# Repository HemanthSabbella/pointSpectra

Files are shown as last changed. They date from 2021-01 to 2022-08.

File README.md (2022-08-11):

# pointSpectra
pointSpectra is a low-cost, open-source alternative for measuring absorbance of the analyte at specific wavelengths of light. This project is initially made to detect various snake species venom in human blood to do a one-to-one mapping of venom and the snake species using Venom Detection Kit. Nevertheless, it  can be used for any analyte.

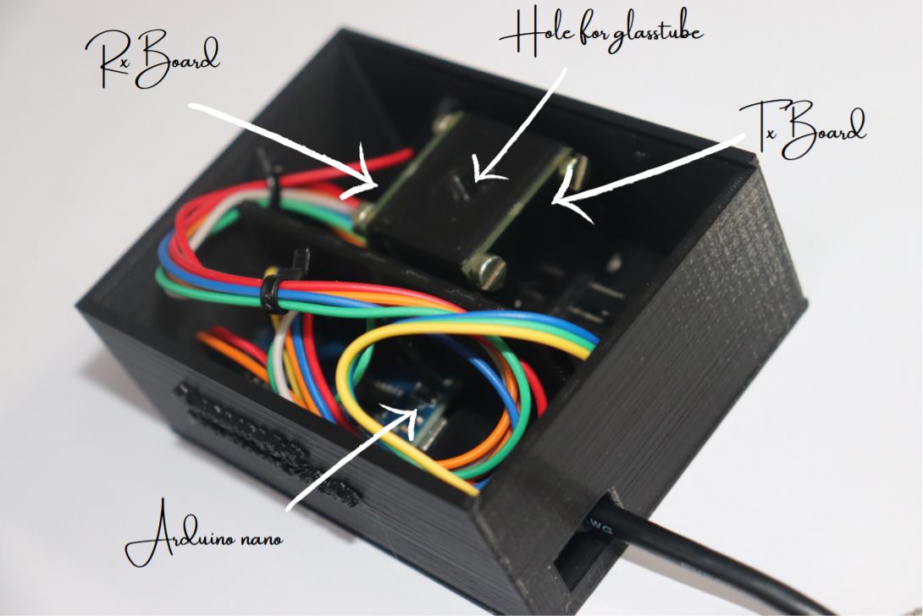
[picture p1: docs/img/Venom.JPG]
> 

**Note:** The whole setup can be built with BOM cost not more than 1000 INR i.e. 15 USD.

# Background

pointSpectra works on the Beer-Lambert law which states that the quantity of light absorbed by a substance dissolved in a fully transmitting solvent is directly proportional to the concentration of the substance and the path length of the light through the solution. The below is the formulation for absorbance of an analyte: 

**Transmittance:**
`T = I / I0`
`% Transmittance: %T = 100 T`

**Absorbance:**
`A = log10 (I0/I)`
`A = log10 (1/T) = -log10 (T)`
`A = log10 (100/%T)`
`A = 2 - log10 (%T)`

# Requirements

**Hardware requirements:**
- [Arduino nano](https://store.arduino.cc/usa/arduino-nano) or [any small form factor arduino](https://store.arduino.cc/usa/arduino/boards-modules)
- [Tx and Rx boards](https://github.com/HemanthSabbella/pointSpectra/tree/main/Tx_Rx_boards%20V1.0)

**Software requirements:**
- [Arduino IDE](https://www.arduino.cc/en/software/)
- [Firmware](https://github.com/HemanthSabbella/pointSpectra/tree/main/firmware)

**Mechanical requirements:**
- [3D-printed case](https://github.com/HemanthSabbella/pointSpectra/tree/main/3D_printed_casing)
- A glass testtube of diameter 5mm.
- Four M3 screws.

# Making 
The setup mainly invoves three boards - Tx Board, Rx Board and Arduino nano. Tx board has wavelength-specific LED emitters that goes through mechanical slits of the 3D printed case in which a glass tube is inserted orthogonally and the unabsorbed light beams coming through the tube, fall on Rx board which has photo diode array that converts the light intensity into proportional frequency. This signal is caputured by the nano-microcontroller, further processing of the data is done and it's followed by plotting the absorbance graph.  

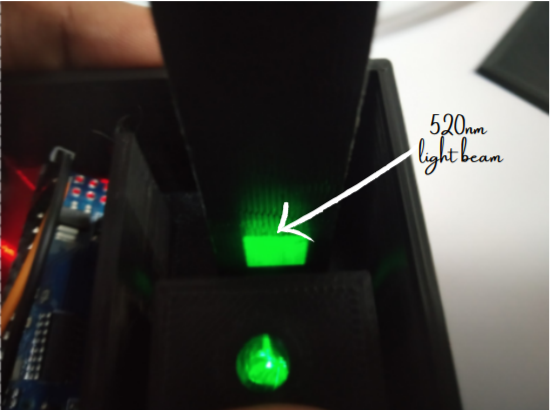
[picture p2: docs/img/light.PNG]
> 
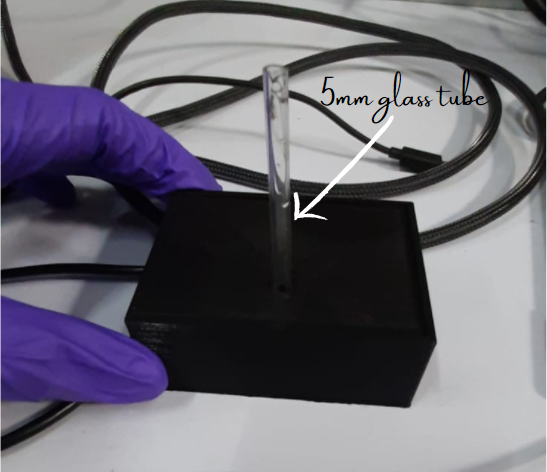
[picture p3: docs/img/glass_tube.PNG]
> 

**Tx Board:** 
- Use narrow-band, dominant wavelength LEDs as light sources for a specific wavelength absorbance. 
- 6-point light sources. 
- Adjust the current limiting resistor properly by using forward voltage and current of LEDs, and the supply voltage. 

Spectral Response of 520nm LED: 

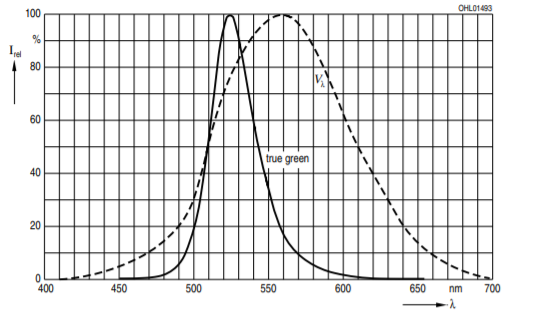
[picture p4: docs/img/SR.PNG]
> 
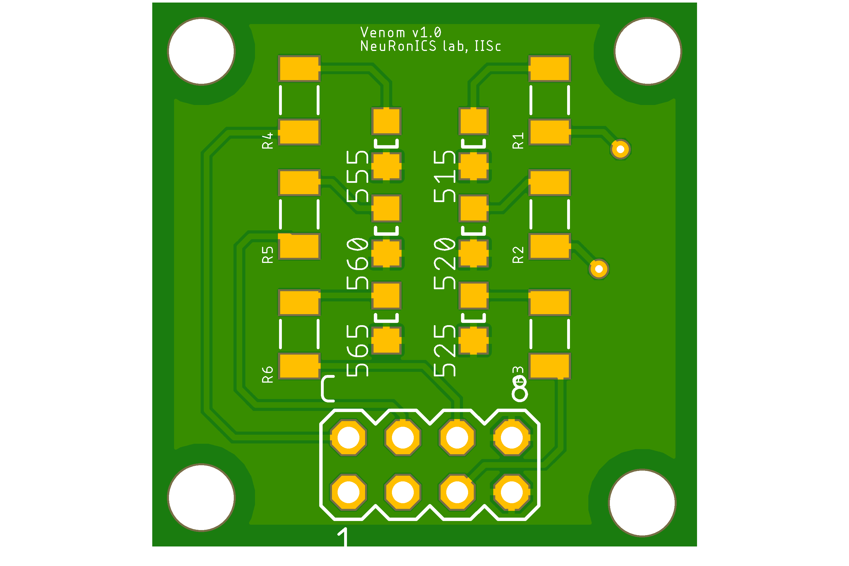
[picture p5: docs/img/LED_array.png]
> 

**Rx Board:**

- TCS3200 - Light (irradiance) to frequency converter. 
- 8 x 8 array of photodiodes. 
- 16 blue filters, 16 green filters, 16 red filters and 16 clear filters. 
- The output is a square wave (50% duty cycle) with frequency directly proportional to luminous intensity (irradiance).

Functional Block Diagram: 

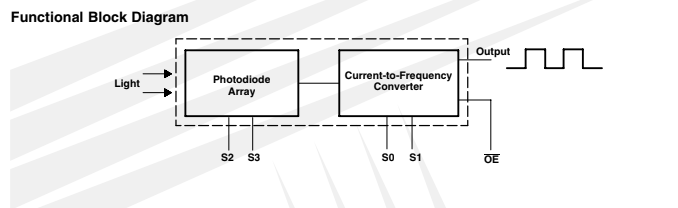
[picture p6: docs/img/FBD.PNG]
> 
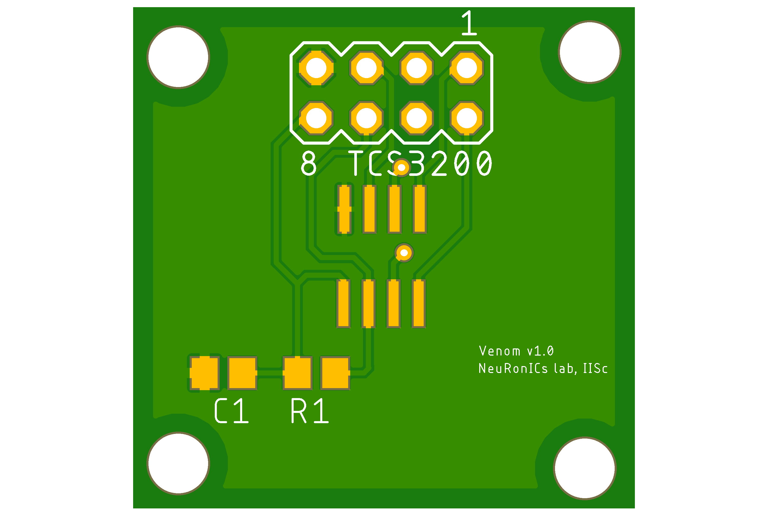
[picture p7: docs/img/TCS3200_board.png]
> 

**3D printed case:**

Use the [cheat sheet](https://github.com/HemanthSabbella/pointSpectra/blob/main/docs/img/3d_print_CS.PNG) of if you are not familiar with 3D printing. We have used fractal works extended printer and print time with infill 50% and layer height 0.2 is 8 hrs. 
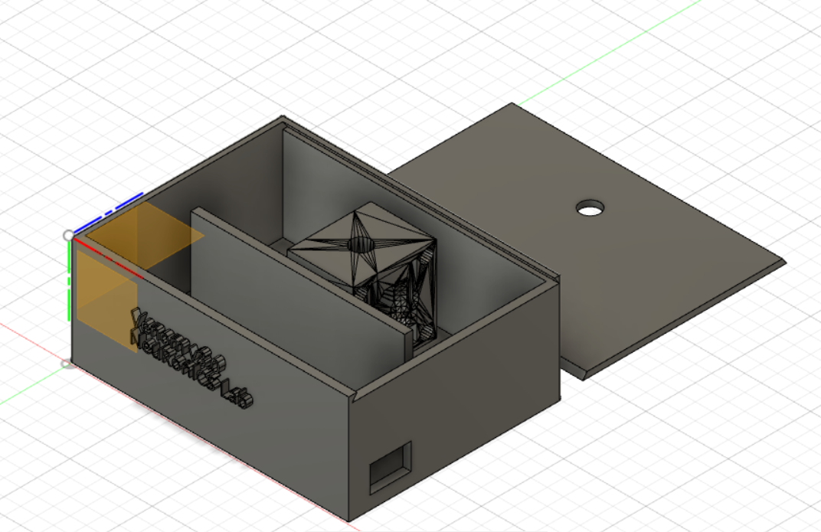
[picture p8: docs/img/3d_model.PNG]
> 

**Pin connections:**

| Tx | Arduino nano|
|------|---------|
| LED_520 | D11 |
| LED_560 | D3 |
| LED_600 | D4 |
| LED_630 | D10 |
| LED_660 | D2 |
| GND | GND |
  
| Rx | Arduino nano|
|--------|---------|
| S0 | D5 |
| S1 | D6 |
| S2 | D7 |
| S3 | D8 |
| sensorOut | D9 |

# Firmware
 The firmware code makes the luminous intensity of LEDs same by adjusting the average current to the LEDs using Pulse Width Modulation (PWM) signals. Standard signal conditioning like moving average on the real-time data is preformed to avoid sharp transition due to external environment. Calibration methods - zero referencing and range mapping are used. It outputs an absorbance graph of an analyte by interpolating the sensor reading of 6 narrow band LED inputs. Flash the [Firmware](https://github.com/HemanthSabbella/pointSpectra/tree/main/firmware) using [Arduino IDE](https://www.arduino.cc/en/software/). 
 
# Results 
 We have measured the absorbance of gold nanoparticles with COVID-19 positive and negative samples at 520nm and 630nm (2-points) and repeated it a couple of times, the results are as below: 
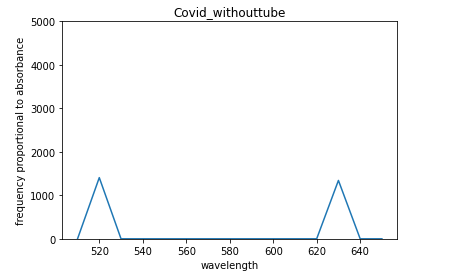
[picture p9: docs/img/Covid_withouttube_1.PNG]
>  <br>
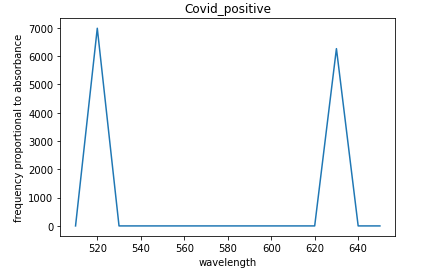
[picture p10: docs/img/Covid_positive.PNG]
>  <br>
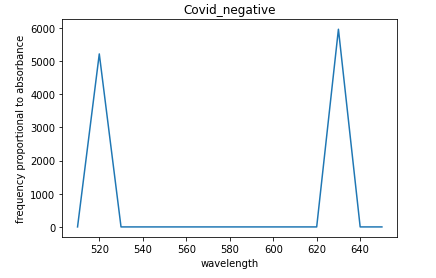
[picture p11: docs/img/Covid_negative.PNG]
> 

# Publication
S C G Kiruba Daniel, Poojitha S Pai, Hemanth Reddy Sabbella, Kumar Singh, Ambica Rangaiah, Shantala Gowdara Basawarajappa, Chetan Singh Thakur, [“Handheld, low-cost, aptamer-based sensing device for rapid SARS-CoV-2 RNA detection using novelly synthesized gold nanoparticles.”](https://ieeexplore.ieee.org/document/9854404) IEEE Sensors Journal, 2022

**Note:** We have been working to test more analytes to validate the robustness of pointSpectra, stay tuned to this space for more results. 

> pointSpectra is developed in [NeuRonICS lab](https://labs.dese.iisc.ac.in/neuronics/), DESE, IISc under the guidance of Dr. Chetan Singh Thakur. For any clarification and details about replication please contact the author at hemanthrs@iisc.ac.in

> Team members: Dr. S. C. G. Kiruba Daniel, Poojitha S Pai

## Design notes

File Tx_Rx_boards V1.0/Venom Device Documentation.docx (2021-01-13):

https://www.arrow.com/en/categories/leds-and-led-lighting/led-indication/leds

https://www.arrow.com/en/categories/leds-and-led-lighting/led-indication/leds?page=1&promoGroupLevel=pl&perPage=25&filters=Dominant%20Wavelength:525;

Narrow-band LEDs with similar luminous intensity:

-> Check the lens appearance specifications:

-> Luminous intensity similar.

-> Wavelength - 520nm and 560 nm.

-> SMD or DIP.

-> If SMD how to focus light as a beam.

3D model:

- V3.1:
  - ~~Add NeuRonICS Lab.~~
  - ~~Space for USB. 12.5 x 8 mm~~
  - ~~Resize the Inner cavity model.~~
  - ~~Resize the M3 screw holes.~~
  - ~~Footprint of the LED board and the detector board.~~
  - Lid: tighten it.
  - ~~Edges more curved on both sides.~~ Did just one more side.
  - ~~Check the light square before - Good getting the square beam of light.~~
  - Any other features to look aesthetic.
- V3.2:
  - Change the cavity with screw fitting. -- This is fine for now. Later maybe.
    - Print this separately for checking the cavity of the test tube.
    - Later: Reduce the small spaces.
    - Screws are fitting good. For Later thread maybe.
  - ~~NeuRonICs size should be equal to venom.~~
  - ~~Align the Cavity with the lid hole.~~

LEDs, wavelength and luminous intensities:

First order:

Component | Luminous Intensity(mcd) | Mouser Link | Qty
LED - SMD - 520nm | 450 mcd | Link (https://www.mouser.in/ProductDetail/Wurth-Elektronik/150080GS75000) | 10
LED - SMD- 525nm | 340 mcd | Link (https://www.mouser.in/ProductDetail/Dialight/599-0181-007F) | 10
LED - SMD- 555nm | 4.5 mcd | Link (https://www.mouser.in/ProductDetail/Bivar/SM0805PGC) | 10
LED - SMD - 560nm | 4 mcd | Link (https://www.mouser.in/ProductDetail/ROHM-Semiconductor/SML-H12P8TT86C) | 10
LED - SMD - 565nm | 10 mcd | Link (https://www.mouser.in/ProductDetail/Lumex/SML-LX0805GC-TR?qs=sGAEpiMZZMseGfSY3csMkW2UPVQWgWXnF7a8MfCoRrI%3D) | 10
Resistor - SMD- 100 ohm1206 | | Link (https://www.mouser.in/ProductDetail/Vishay-Dale/RCS1206100RFKEA) | 10
Resistor - SMD-150 ohm 1206 | | Link (https://www.mouser.in/ProductDetail/Vishay-Dale/RCS1206150RFKEA) | 10
Capacitor - SMD- 0.1uF 0805 | | Link (https://www.mouser.in/ProductDetail/Taiyo-Yuden/TMF212B7104MGHT) | 10
TCS3200 - Color light to frequency converter. | | Link (https://www.mouser.in/ProductDetail/ams/TCS3200D-TR?qs=sGAEpiMZZMvaelWNQAznkVDXmuGu5Gi9) | 5

Second order:

Wavelength | Luminous Intensity | Manufacturer Number | Quantity | Mouser Link
525 nm | 150 mcd | 859-LTST-C170TGKT | 10 | Link (https://www.mouser.in/ProductDetail/859-LTST-C170TGKT)
630 nm | 150 mcd | 604-APTD2012LSURCK | 10 | Link (https://www.mouser.in/ProductDetail/604-APTD2012LSURCK)
562 nm (0603) | 82 mcd | 327-VFHL1116P4BX3CTR | 5 | Link (https://www.mouser.in/ProductDetail/327-VFHL1116P4BX3CTR)
528 nm (0603) | 90 mcd | 720-LTL29SN2Q125Z | 5 | Link (https://www.mouser.in/ProductDetail/720-LTL29SN2Q125Z)
605 nm | 150 mcd | 604-APT2012LSECKJ4RV | 5 | Link (https://www.mouser.in/ProductDetail/604-APT2012LSECKJ4RV)

Problem: Resistor for 630nm! -> 2k IS NEEDED -> you have 1k so just use a wire to short on 1k to other 1k.

Third order:

Wavelength | Luminous Intensity | Manufacturer Number | Quantity | Mouser Link
642nm | 80mcd | 598-8110-102F | 10 | Link (https://www.mouser.in/ProductDetail/Dialight/598-8110-102F?qs=Te4RMVqx8WLRPJkTI3mDJA%3D%3D)
660nm | 100mcd | SML-LXFM0603SRC-TR | 10 | Link (https://www.mouser.in/ProductDetail/Dialight/598-8110-102F?qs=Te4RMVqx8WLRPJkTI3mDJA%3D%3D)

Scripts for plots and averaging: https://colab.research.google.com/drive/1RDzzlXy0TrXJwmM4R60sGGzhkmMovc6T#scrollTo=2AHoIRS3nakt

Results from the device:

Send graphs for this: DATA analysis properly.

COVID results using the device.

Tube contents | f(520nm wavelength) | f(630nm wavelength)
Control | 4118 | 5293
Positive | 6984 | 6264
Negative | 5220 | 5964
Without tube | 1406 | 1342

Venom results using a Venom-D prototype device.

Samples test 2:

Tube contents | f(520nm wavelength) | f(630nm wavelength)
Positive | 5368 | 6625
Negative | 6002 | 5620
Without tube | 1406 | 1342

Samples test 3:

Tube contents | f(520nm wavelength) | f(630nm wavelength)
Positive | 5719 | 7241
Negative | 6966 | 4430
Without tube | 1305 | 1390

To do :

- Order more LEDs.
  - Check the near intensity.
  - Footprint.
  - Current limiting resistor.
  - 650nm, 675nm, 700nm, 725nm, 750nm, 775nm, 800nm(check near if it’s not there!)
  - Maybe order also 500nm, 475nm, 450nm, 425nm, 400nm.
- Check with different LEDs and interpolate the results. Use a good current limiting resistor for equal intensity and solder it on to the board.
- Tune to minimize the delta from 50 to 5! i.e make the readings of the both the wavelengths same in the device without anything.

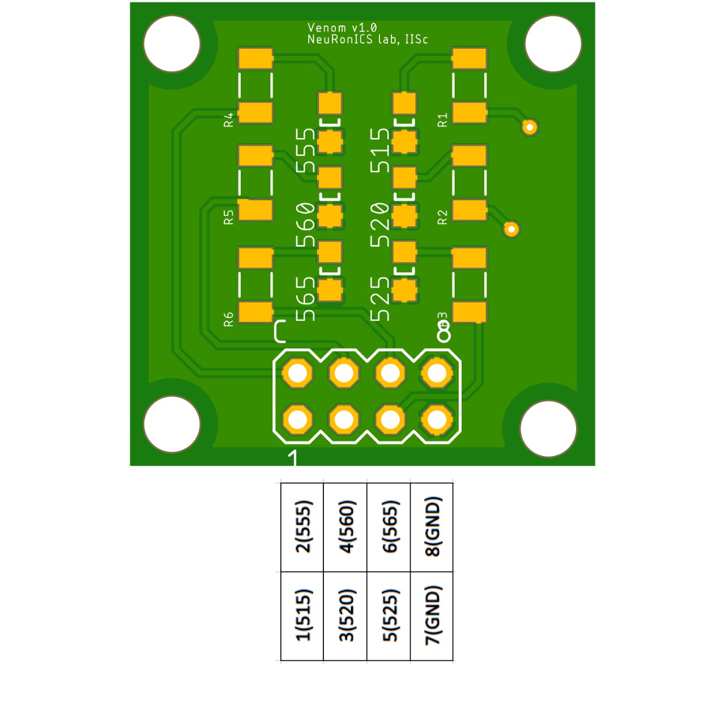
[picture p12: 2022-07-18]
docs/Tx_Physical_Pins.JPG

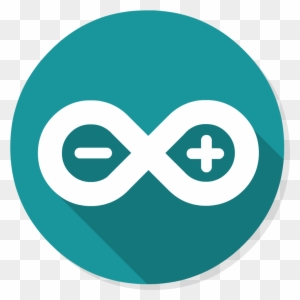
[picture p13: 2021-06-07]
docs/img/arduino_ide.png

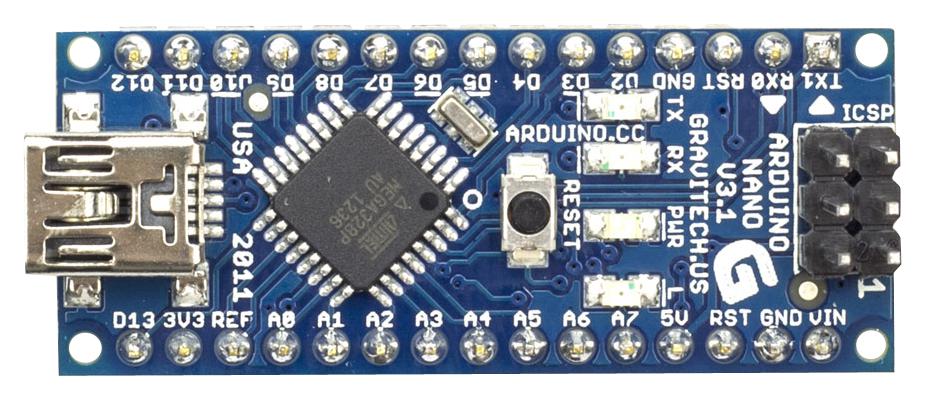
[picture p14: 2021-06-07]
docs/img/nano.jpg

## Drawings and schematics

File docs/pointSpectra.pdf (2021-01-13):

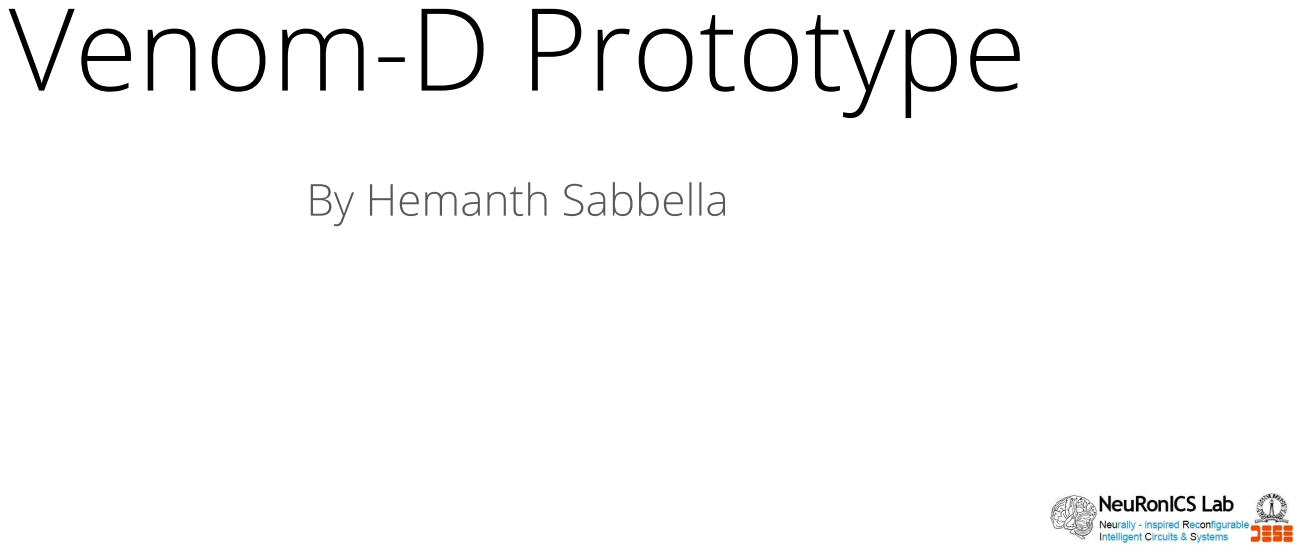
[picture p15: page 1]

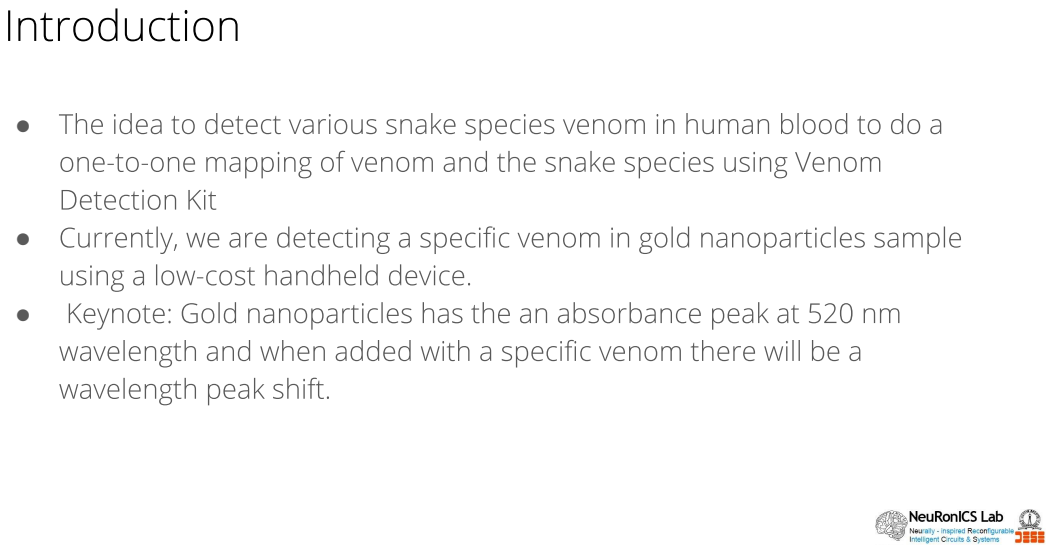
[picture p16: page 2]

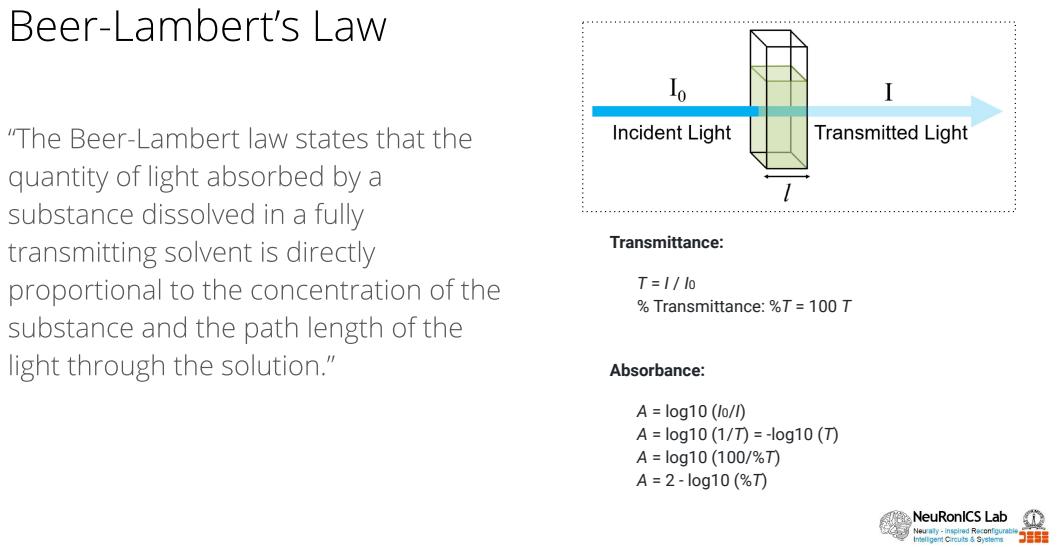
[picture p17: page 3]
Transmittance:; Absorbance:

T = I / I0
% Transmittance: %T = 100 T

A = log10 (I0/I)
A = log10 (1/T) = -log10 (T)
A = log10 (100/%T)
A = 2 - log10 (%T)

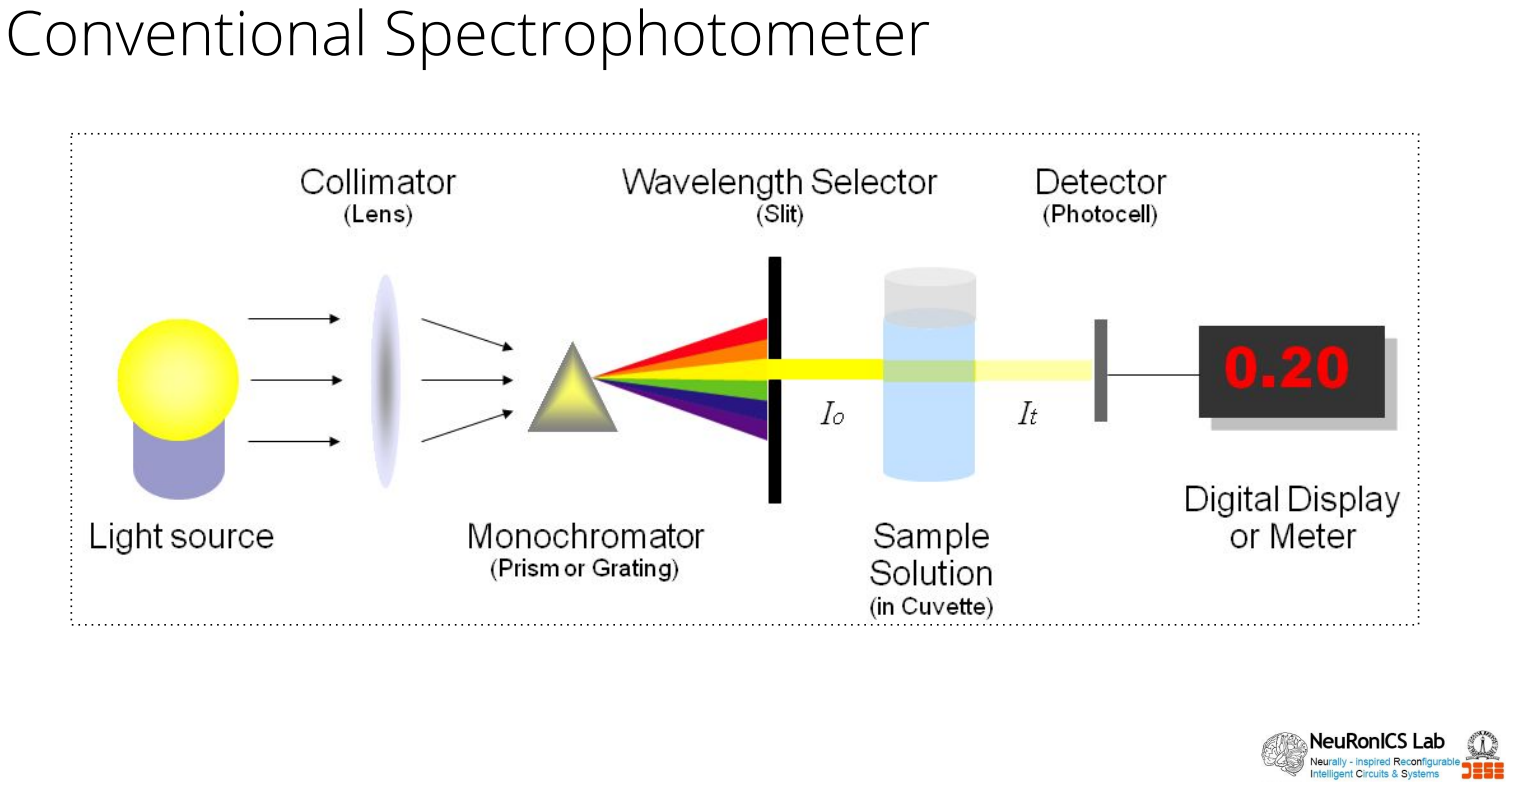
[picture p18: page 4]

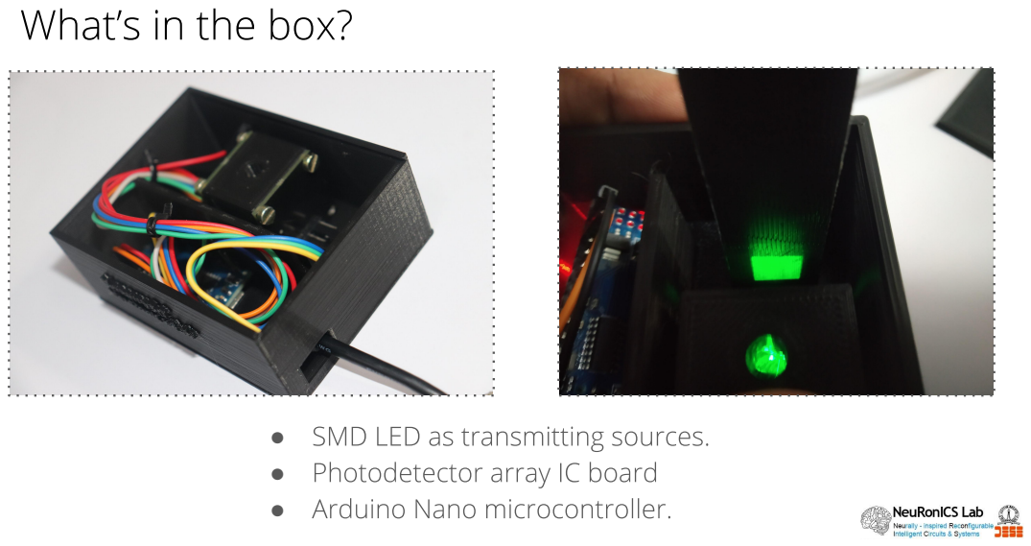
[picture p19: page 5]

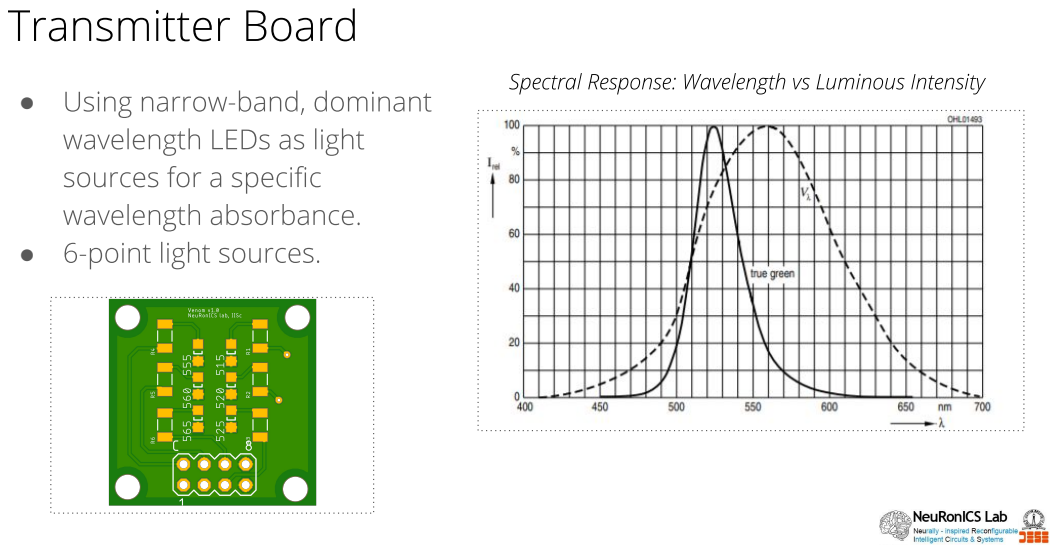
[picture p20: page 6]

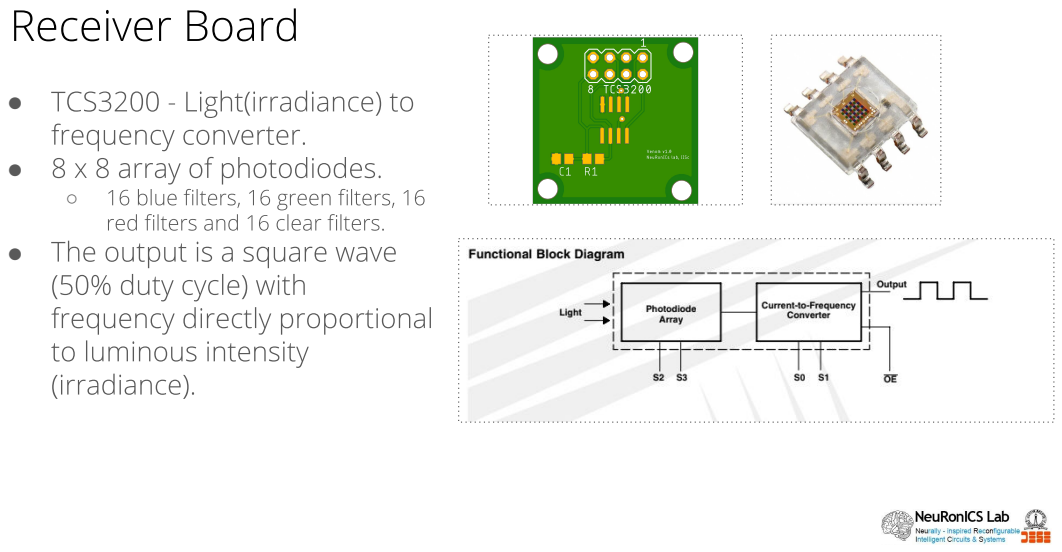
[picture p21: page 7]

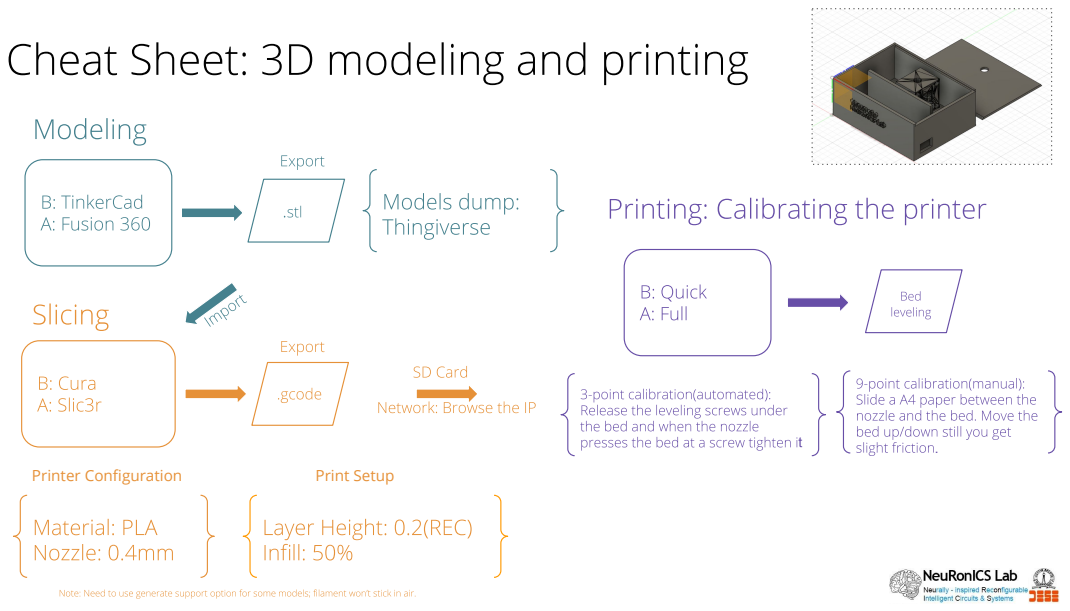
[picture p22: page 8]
Printer Configuration; Print Setup

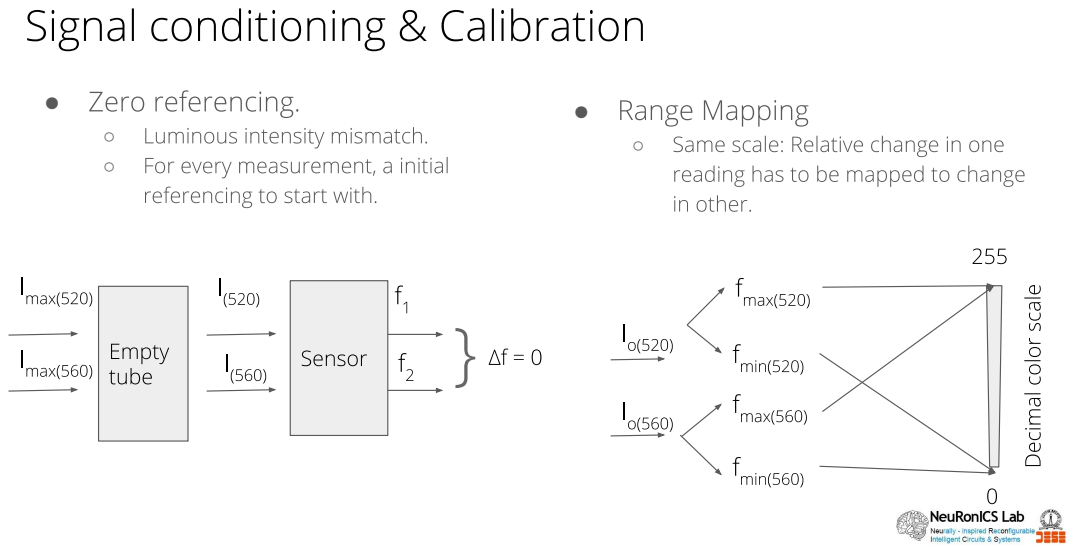
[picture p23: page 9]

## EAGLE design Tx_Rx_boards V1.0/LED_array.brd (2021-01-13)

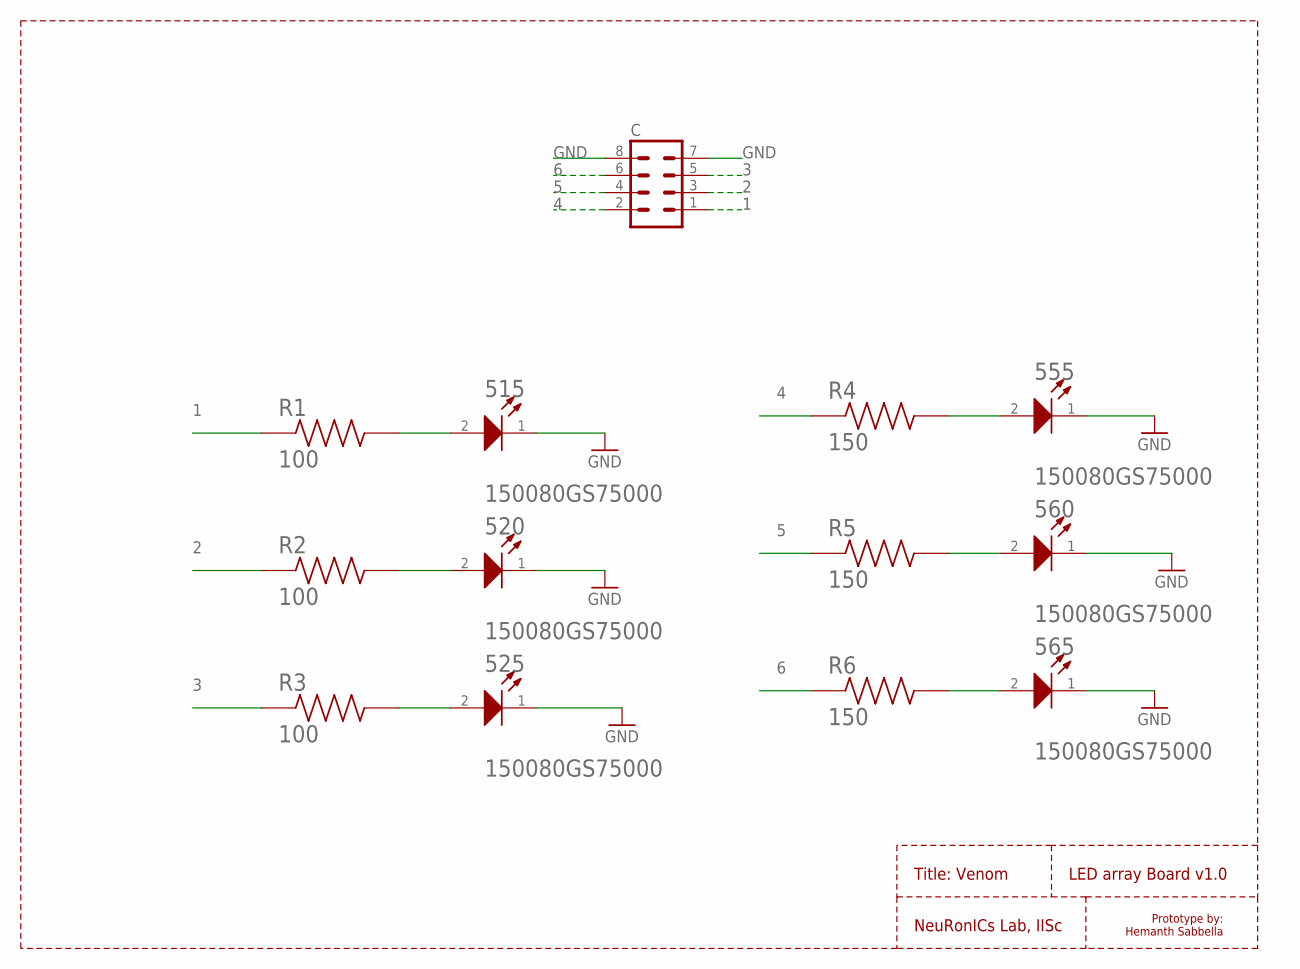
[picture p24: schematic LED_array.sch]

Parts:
515, 520, 525, 555, 560, 565: WUERTH_ELEKTRONIK_150080GS75000WUERTH_ELEKTRONIK_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; WUERTH_ELEKTRONIK_150080GS75000_0
C: MA04-2
R1, R2, R3: 100; RESC3116X65N
R4, R5, R6: 150; RESC3116X65N

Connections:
1: C.1, R1.1
2: C.3, R2.1
3: C.5, R3.1
4: C.2, R4.1
5: C.4, R5.1
6: C.6, R6.1
GND: 515.1 (K), 520.1 (K), 525.1 (K), 555.1 (K), 560.1 (K), 565.1 (K), C.7, C.8
unnamed: 555.2 (A), R4.2
unnamed: 560.2 (A), R5.2
unnamed: 565.2 (A), R6.2
unnamed: 515.2 (A), R1.2
unnamed: 520.2 (A), R2.2
unnamed: 525.2 (A), R3.2

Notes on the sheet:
Title: Venom
Prototype by: Hemanth Sabbella
NeuRonICs Lab, IISc
LED array Board v1.0

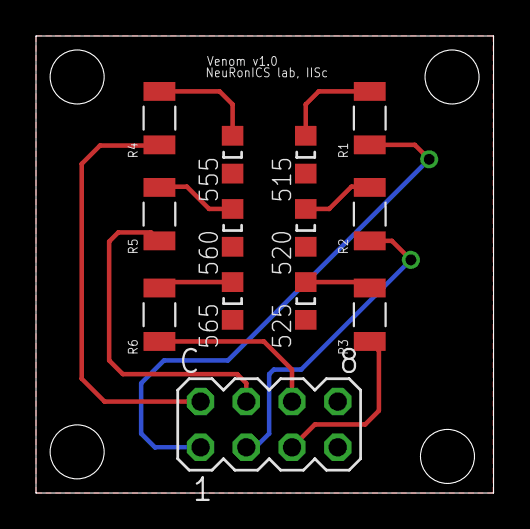
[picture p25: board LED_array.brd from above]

Board: 2 copper layers, 25.4 x 25.4 mm, 13 parts (0 on the bottom side), 13 nets.

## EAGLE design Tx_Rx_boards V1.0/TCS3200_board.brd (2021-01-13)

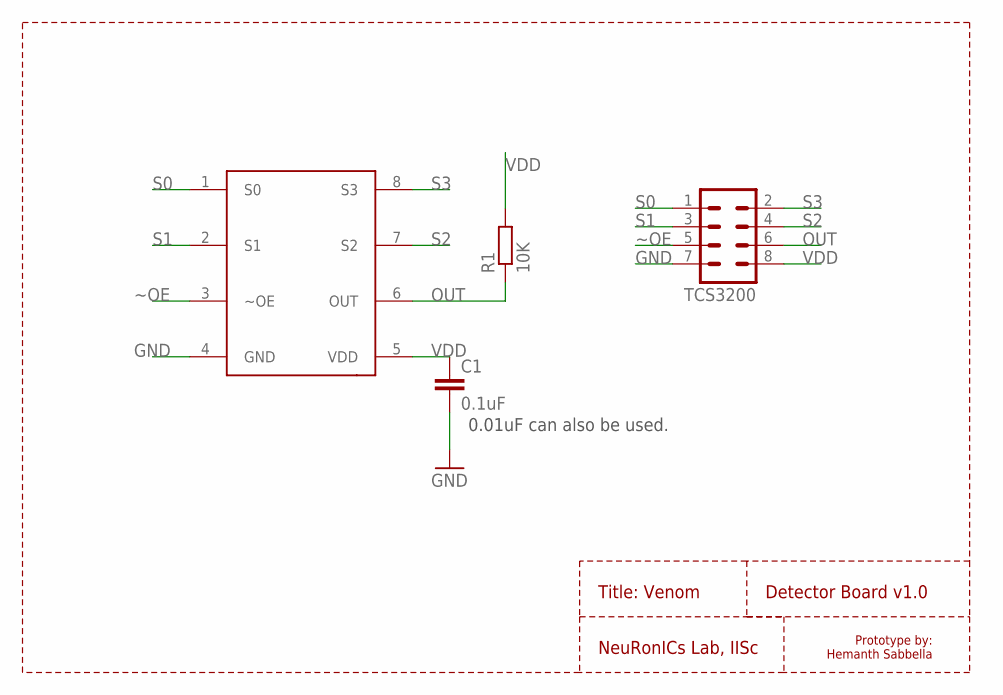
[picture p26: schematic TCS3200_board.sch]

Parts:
C1: 0.1uF; C0805
R1: 10K; R0805
TCS3200: MA04-2
U$1: TCS3200

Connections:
GND: C1.2, TCS3200.7, U$1.4 (GND)
OUT: R1.1, TCS3200.6, U$1.6 (OUT)
S0: TCS3200.1, U$1.1 (S0)
S1: TCS3200.3, U$1.2 (S1)
S2: TCS3200.4, U$1.7 (S2)
S3: TCS3200.2, U$1.8 (S3)
VDD: C1.1, R1.2, TCS3200.8, U$1.5 (VDD)
~OE: TCS3200.5, U$1.3 (~OE)

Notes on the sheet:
0.01uF can also be used.
Title: Venom
Prototype by: Hemanth Sabbella
NeuRonICs Lab, IISc
Detector Board v1.0

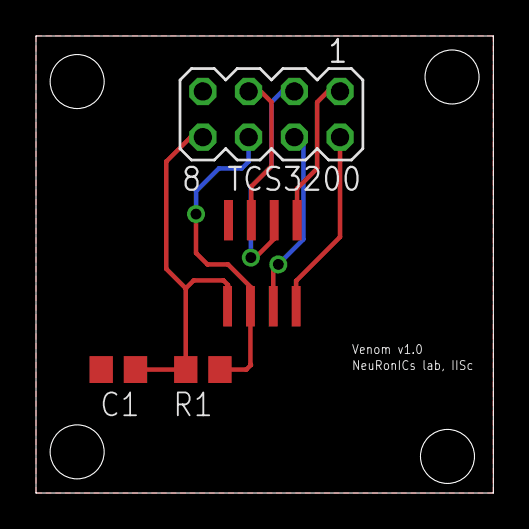
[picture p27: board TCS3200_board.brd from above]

Board: 2 copper layers, 25.4 x 25.4 mm, 4 parts (0 on the bottom side), 8 nets.

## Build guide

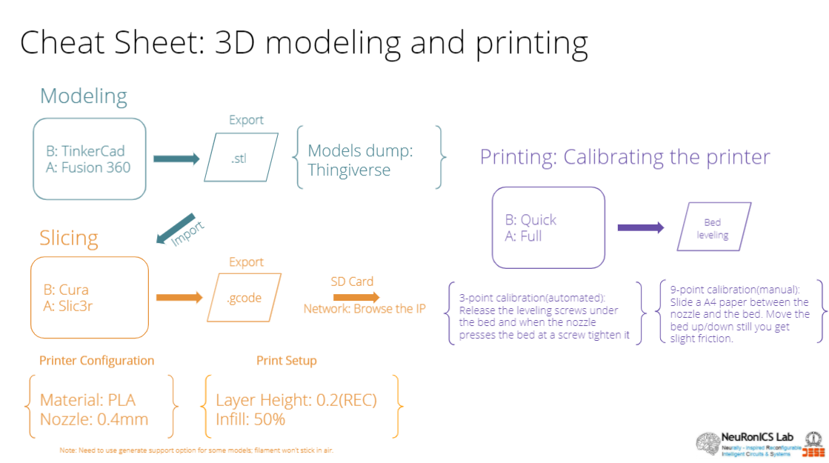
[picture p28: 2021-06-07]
docs/img/3d_print_CS.PNG

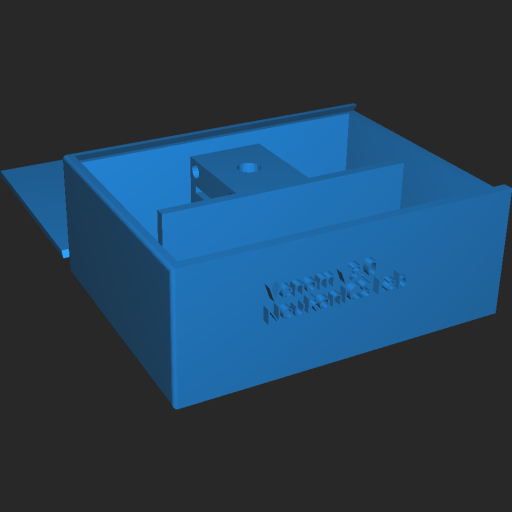
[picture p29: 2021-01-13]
3D_printed_casing/Venom_final V3.png

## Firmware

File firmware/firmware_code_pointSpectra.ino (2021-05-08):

/* pointSpectra
  Author: Hemanth Sabbella
  Advisor: Dr. Chetan Singh Thakur
  Copyright © NeuRonICS Lab, IISc
*/

/*
 * 
 * Pin connections
 * Arduino Nano -> Transmitter board; Arduino Nano -> Receiver board.
 * 
 */
#define S0 5
#define S1 6
#define S2 7
#define S3 8
#define LED_520 11
#define LED_560 3
#define LED_600 4
#define LED_630 10 // 520 pads on the board
#define LED_660 2
#define sensorOut 9

/*
 * Variable initializations.
 */
int count = 0;
int average_count = 100; // 5 seconds averaging value; the loop has 100 ms delay in it so counting 50 times to get 5 seconds.
float initial_value = 0;
float reference_value = 0;

float frequency_520 = 0;
float average_f_520 = 0;
float frequency_560 = 0;
float average_f_560 = 0;
float frequency_600 = 0;
float average_f_600 = 0;
float frequency_630 = 0;
float average_f_630 = 0;
float frequency_660 = 0;
float average_f_660 = 0;

float normalized_wavelength_green = 500;
float normalizing_factor_green = 0.6; 
float nomralized_wavelength_red = 650;
float normalizing_factor_red = 0.8; //650nm
float normalized_520;
float normalized_560;
float normalized_600;
float normalized_630;
float normalized_660;


float slope;
float constant = 0.06;
void setup() {
  pinMode(S0, OUTPUT);
  pinMode(S1, OUTPUT);
  pinMode(S2, OUTPUT);
  pinMode(S3, OUTPUT);
  pinMode(sensorOut, INPUT);
  pinMode(LED_520, OUTPUT);
  pinMode(LED_630, OUTPUT);

  //Setting frequency-scaling to 100%, clear photodiode type, no filters!
  digitalWrite(S0, HIGH);
  digitalWrite(S1, LOW);
  digitalWrite(S2, HIGH);
  digitalWrite(S3, HIGH);

  Serial.begin(9600);
  
//  //checking the reference value(i.e average of readings for 5s) which is the value of the sensor in the current setup and environment. 
//  Serial.print("Checking reference value:");
//  while(count < average_count){
//    initial_value = pulseIn(sensorOut, HIGH);
//    reference_value = reference_value + initial_value;
//    delay(100);
//    count = count + 1;
//    //Serial.println(initial_value);
//  }
//  count = 0;
//  Serial.println(reference_value/(float)average_count);
//
  //Calulating slope of the spectral response cruver for the TCS3200
  slope = (normalizing_factor_red - normalizing_factor_green)/(nomralized_wavelength_red - normalized_wavelength_green);
  normalized_520 = slope*520 - constant;
  normalized_560 = slope*560 - constant;
  normalized_600 = slope*600 - constant;
  normalized_630 = slope*630 - constant;
  normalized_660 = slope*660 - constant;
////  Serial.print("normalized_520:");
////  Serial.println(normalized_520);
////  Serial.print("normalized_560:");
////  Serial.println(normalized_560);
////  Serial.print("normalized_600:");
////  Serial.println(normalized_600);
////  Serial.print("normalized_630:");
////  Serial.println(normalized_630);
////  Serial.print("normalized_660:");
////  Serial.println(normalized_660);
//
//  /*
// * 520 nm frequency readings average 
// */
//  Serial.print("Average_Frequency of 520nm:");
//  digitalWrite(LED_520, HIGH);
//  while(count < average_count){
//    frequency_520 = pulseIn(sensorOut, HIGH);
//    average_f_520 = average_f_520 + frequency_520;
//    delay(100);
//    count = count + 1;
//  }
//  digitalWrite(LED_520, LOW);
//  Serial.println(normalized_520*(average_f_520/(float)average_count));
//  count = 0;
//  average_f_520 = 0;
//  delay(1000);
//
//
//
//
///*
// * 560 nm frequency readings average 
// */
//  Serial.print("Average_Frequency of 560nm:");
//  digitalWrite(LED_560, HIGH);
//  while(count < average_count){
//    frequency_560 = pulseIn(sensorOut, HIGH);
//    average_f_560 = average_f_560 + frequency_560;
//    delay(100);
//    count = count + 1;
//  }
//  digitalWrite(LED_560, LOW);
//  Serial.println(normalized_560*(average_f_560/(float)average_count));
//  count = 0;
//  average_f_560 = 0;
//  delay(1000);
//
//
///*
// * 600 nm frequency readings average 
// */
//  Serial.print("Average_Frequency of 600nm:");
//  digitalWrite(LED_600, HIGH);
//  while(count < average_count){
//    frequency_600 = pulseIn(sensorOut, HIGH);
//    average_f_600 = average_f_600 + frequency_600;
//    delay(100);
//    count = count + 1;
//  }
//  digitalWrite(LED_600, LOW);
//  Serial.println(normalized_600*(average_f_600/(float)average_count));
//  count = 0;
//  average_f_600 = 0;
//  delay(1000);
//
//
//
///*
// * 630 nm frequency readings average 
// */
//  Serial.print("Average_Frequency of 630nm:");
//  digitalWrite(LED_630, HIGH);
//  while(count < average_count){
//    frequency_630 = pulseIn(sensorOut, HIGH);
//    average_f_630 = average_f_630 + frequency_630;
//    delay(100);
//    count = count + 1;
//  }
//  digitalWrite(LED_630, LOW);
//  Serial.println(normalized_630*(average_f_630/(float)average_count));
//  count = 0;
//  average_f_630 = 0;
//  delay(1000);
//
//
///*
// * 660 nm frequency readings average 
// */
//  Serial.print("Average_Frequency of 660nm:");
//  digitalWrite(LED_660, HIGH);
//  while(count < average_count){
//    frequency_660 = pulseIn(sensorOut, HIGH);
//    average_f_660 = average_f_660 + frequency_660;
//    delay(100);
//    count = count + 1;
//  }
//  digitalWrite(LED_660, LOW);
//  Serial.println(normalized_660*(average_f_660/(float)average_count));
//  count = 0;
//  average_f_660 = 0;
//  delay(1000);
//  
}


void loop() {
/*
 * 520 nm frequency readings average 
 */
  Serial.print("Average_Frequency of 520nm:");
  analogWrite(LED_520, 110); //110 -> 750
  while(count < average_count){
    frequency_520 = pulseIn(sensorOut, HIGH);
    //Serial.println(frequency_520);
    average_f_520 = average_f_520 + frequency_520;
    delay(100);
    count = count + 1;
  }
 analogWrite(LED_520, 0);
 Serial.println(normalized_520*(average_f_520/(float)average_count));
 count = 0;
 average_f_520 = 0;
 delay(1000);

 /*
 * 630 nm frequency readings average 
 */
  Serial.print("Average_Frequency of 630nm:");
  analogWrite(LED_630, 200); //200 -> 750
  while(count < average_count){
    frequency_630 = pulseIn(sensorOut, HIGH);
    average_f_630 = average_f_630 + frequency_630;
    delay(100);
    count = count + 1;
  }
  analogWrite(LED_630, 0);
  Serial.println(normalized_630*(average_f_630/(float)average_count));
  count = 0;
  average_f_630 = 0;
  delay(1000);

//analogWrite(LED_520, 200);
//initial_value = pulseIn(sensorOut, HIGH);
////analogWrite(LED_520, 0);
//Serial.print("520nm:");
//Serial.println(initial_value);
//delay(1000);
//analogWrite(LED_630, 255);
//initial_value = pulseIn(sensorOut, HIGH);
//delay(5000);
//analogWrite(LED_630, 0);
//Serial.print("630nm:");
//Serial.println(initial_value);
//delay(1000);

}

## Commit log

2021-01-13 Updated Venom PCB files, 3D casing files and the presentation
    [Arduino_mount.sch, LED_array.brd, LED_array.sch, TCS3200_board.brd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]
2021-05-08 Changes the name of the device
    [Arduino_mount.sch, LED_array.brd, LED_array.sch, TCS3200_board.brd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]
2021-05-08 Added firmware, changes the folder names
    [Arduino_mount.sch, LED_array.brd, LED_array.sch, TCS3200_board.brd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]
2021-06-07 Added boards
